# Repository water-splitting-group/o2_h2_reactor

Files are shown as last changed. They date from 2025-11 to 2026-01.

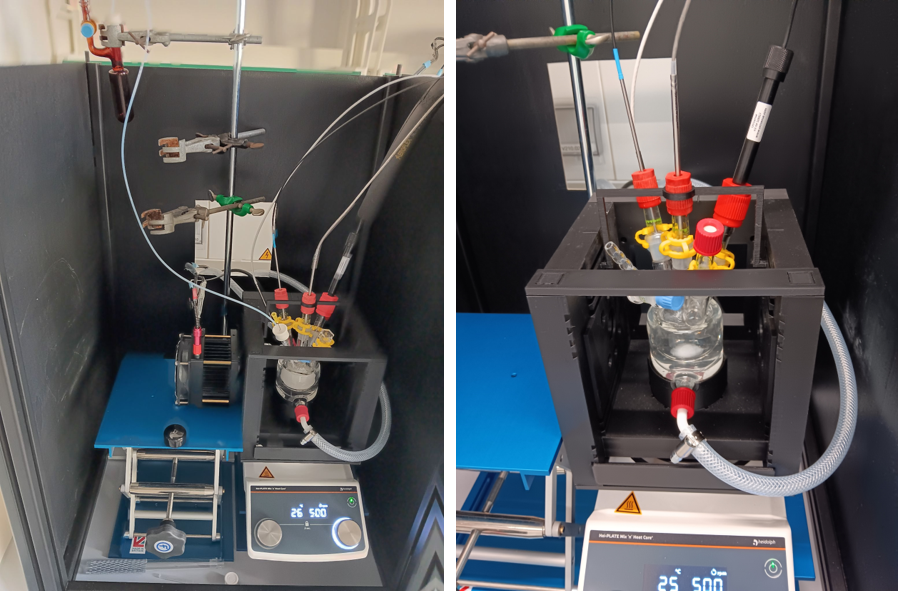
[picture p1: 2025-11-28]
figures/irrad_setup_chamber.png

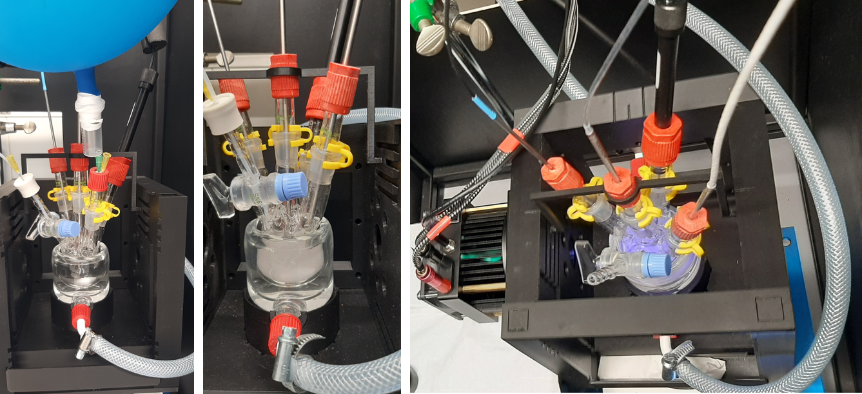
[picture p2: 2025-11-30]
figures/test_main_steps.png

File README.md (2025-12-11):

# Overview

This repository contains original data and analysis code for "Simultaneous in situ oxygen and hydrogen detection during photocatalytic water splitting".

`documents` contains manuscript and supporting information.

`experimental_data` contains experimental data, both from photocatalytic experiments, and photocatalyst characterization.

`figures` contains figures that appear in  manuscript and supporting information.

`irradiation_setup` contains files and instructions to build the setup provided in the manuscript.

`labjournal_entries` contains electronic labjournal entries of all relevant photocatalytic and synthetic experiments, general protocols (including calibration procedures, standard procedures for in situ measurements etc.), design and 3D printing of the setup compartments, as well as the devices entries in the form of .pdf files.

Subdirectories contain separate README.md files which detail their contents.

We actively encourage others to work on this interesting new avenue in automatization, are happy to answer questions or comments and are open to cooperations in this field.

# License

Copyright (c) Nadzeya Brezhneva, Alexander Eith, Ebrahim Abedini, Jacob Schneidewind

All software is licensed under a MIT license (see `LICENSE` file).

Shield: [][cc-by]

All other files and their contents are licensed under a
[Creative Commons Attribution 4.0 International License][cc-by]. (see `LICENSE-CC-BY`)

[][cc-by]

[cc-by]: http://creativecommons.org/licenses/by/4.0/
[cc-by-image]: https://i.creativecommons.org/l/by/4.0/88x31.png
[cc-by-shield]: https://img.shields.io/badge/License-CC%20BY%204.0-lightgrey.svg

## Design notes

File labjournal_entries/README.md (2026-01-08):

# General

This directory contains labjournal entries.

`equipment` contains labjournal entries of the used devices 

`general_protocols` contains labjournal entries of the used general protocols 

`irradiation_experiments` contains labjournal entries for all photocatalytic tests

`irradiation setup` contains labjournal entries for construction of irradiation chambers, 4-neck photoreactor

`synthesis_experiments` contains labjournal entries for photocatalyst preparation

`calibration_experiments` contains labjournal entries for calibration of Unisense and Pyroscience sensors

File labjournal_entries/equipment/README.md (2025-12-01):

# General

This directory contains labjournal entries of the used devices.

`3d_printer` contains info about model of the used 3D printer,

`18a_power_source` contains info about power supply,

`365_uhp_led` contains info about 365 nm LED,

`firesting_o2_meter` contains info about oxygen meter,

`h2_sensor` contains info about sensor used for hydrogen measurements in gas and liquid phase,

`irradiation_chamber` contains info about advanced irradiation chamber where irraiation was performed,

`irradiation_setup` contains info about irradiation setup where irradiation and measurements were performed,

`o2_h2_reactor` contains info about 4-neck photoreactor for O2 and H2 simultaneous measurements,

`power_meter` contains info about power meter and thermopile sensor used for adjusting LED power before photocatalytic tests,

`robust_probe_o2` contains info about sensor used for oxygen measurements in gas and liquid phase,

`unisense_h2_meter`contains info about amplifier for H2 sensor,

`vortexer` contains info about vortex mixer used for photocatalyst suspension preparation

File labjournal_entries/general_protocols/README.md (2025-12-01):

# General

This directory contains labjournal entries of the general procedures used in work.

`firesting_software` contains info about procedure for in situ O2 measurements using Pyroscience Workbench software,

`gas_phase_h2_calib` contains info about procedure of H2 sensor calibration in gas phase,

`hydrogen` contains info about the procedure of getting and transfer of H2 gas using balloon,

`in-situ_h2_o2_measurement` contains info about main steps for simultaneous in situ O2 and H2 measurements in photocatalytic tests,

`liquid_phase_h2_calib` contains info about procedure of H2 sensor calibration in liquid phase,

`power_determination` contains info about determination of the required analogue setting of power source for desired power output,

`settings_3d_printer` contains overview of standard settings for 3D printer,

`use_3d_printer` contains the procedure of 3D printing of the desired model

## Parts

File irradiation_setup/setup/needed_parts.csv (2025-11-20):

part | amount needed
aluminium profiles (nut 8, type I, black) 40x40x400 mm | 2
aluminium profiles (nut 8, type I, black) 40x40x420 mm | 2
aluminium profiles (nut 8, type I, black) 40x40x700 mm | 4
wood plate 675x443x6 mm | 2
wood plate 675x493x6 mm | 1
wood plate 675x493x6 mm, with cutout 220 mm above bottom edge 150x150 mm | 1
wood plate 550x500x6 mm | 1
lab jack | 2
laboratory stand | 1

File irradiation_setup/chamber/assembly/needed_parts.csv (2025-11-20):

part | amount needed
back_wall_v1-0 | 1
side_walls_v1-0 | 1
bottom_wall_v1-0 | 1
aperture_double_walled_beaker_v1-0 | 1
aperture_dummy_v1-0 | 1
aperture_led_v1-0 | 1
holder_o2_h2_reactor_v1-0 | 1
stabilizer_v1-0 | 2
3mm nuts DIN439 | 8
M3x25 screws DIN912 | 8
double_walled_beaker | 1
power strips | 2
LCS-0365-76-22 super high power LED from Mightex | 1
BLS-18000-1 power supply from Mightex | 1
water tubing | approx. 2 meters
LOOP Thermoelectric thermostat L100 thermostat from Lauda | 1
tubing connectors | 4

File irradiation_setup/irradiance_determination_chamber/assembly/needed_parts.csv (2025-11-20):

part | amount needed
back_wall_v1-1 | 1
side_walls_v1-0 | 1
bottom_wall_v1-0 | 1
front_wall_v1-0 | 1
lid_v1-0 | 1
aperture_dummy_v1-0 | 1
aperture_led_v1-0 | 1
aperture_power_sensor_v1-0 | 1
holder_power_sensor_v1-0 | 1
3mm nuts DIN439 | 8
M3x25 screws DIN912 | 8
LCS-0365-76-22 super high power LED from Mightex | 1
BLS-18000-1 power supply from Mightex | 1
843-R-USB power meter from Newport | 1
919P-020-12 power sensor from Newport | 1

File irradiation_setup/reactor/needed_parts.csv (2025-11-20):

part | amount needed
reactor | 1
transition piece NS14 to GL14 | 4
transition piece NS14 to GL18 | 1

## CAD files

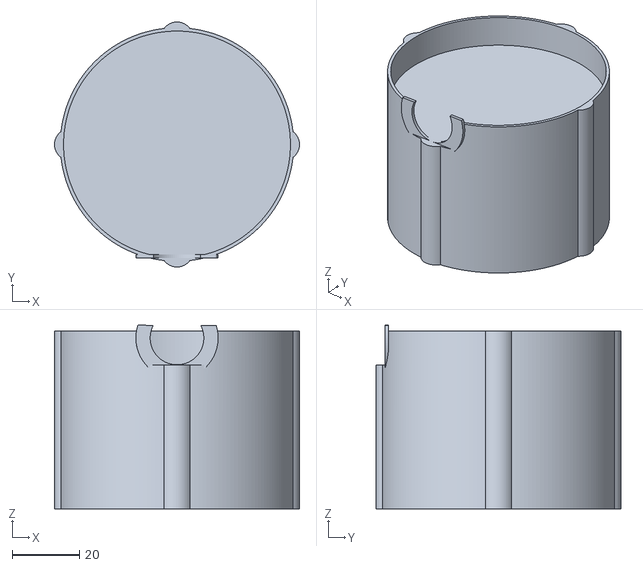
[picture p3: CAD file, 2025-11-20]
irradiation_setup/chamber/apertures/aperture_double_walled_beaker_v1-0.stl
73.0 x 73.0 x 54.7

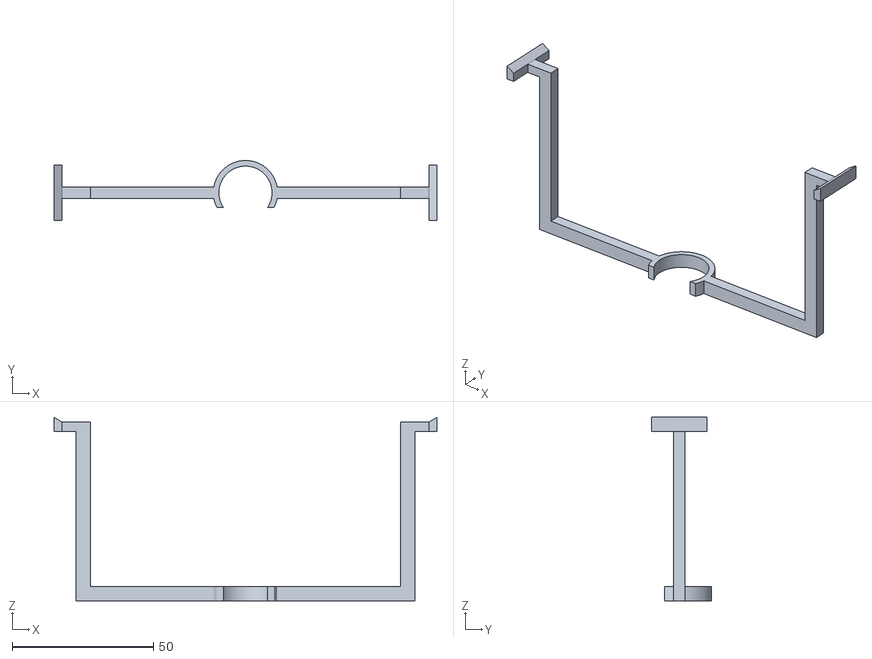
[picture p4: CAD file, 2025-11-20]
irradiation_setup/chamber/holder/holder_o2_h2_reactor_v0-3.stl
135.6 x 21.2 x 65.0

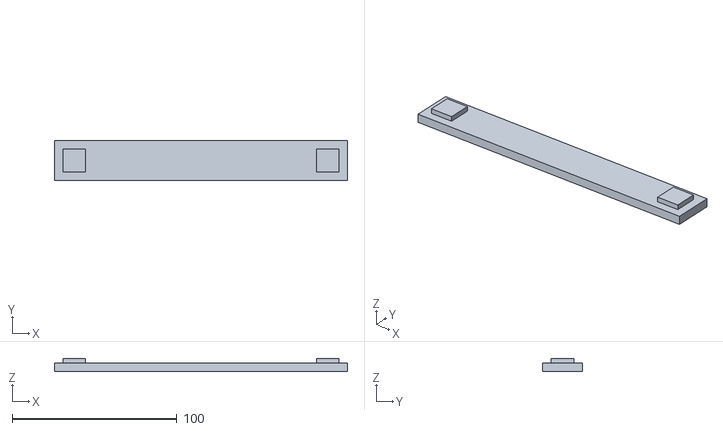
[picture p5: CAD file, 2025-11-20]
irradiation_setup/chamber/other/stabilizer_v1-0.stl
178.0 x 24.0 x 7.85

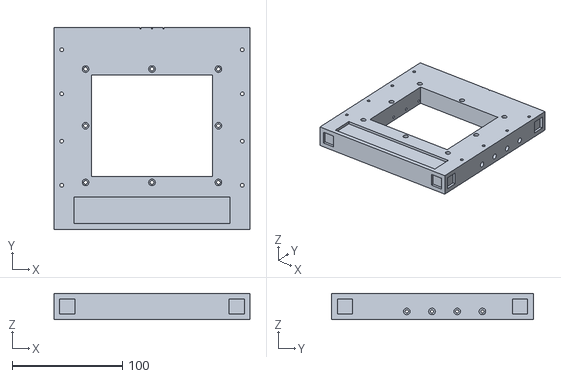
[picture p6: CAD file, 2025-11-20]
irradiation_setup/chamber/walls/back_wall_v1-0.stl
178.0 x 183.0 x 24.0

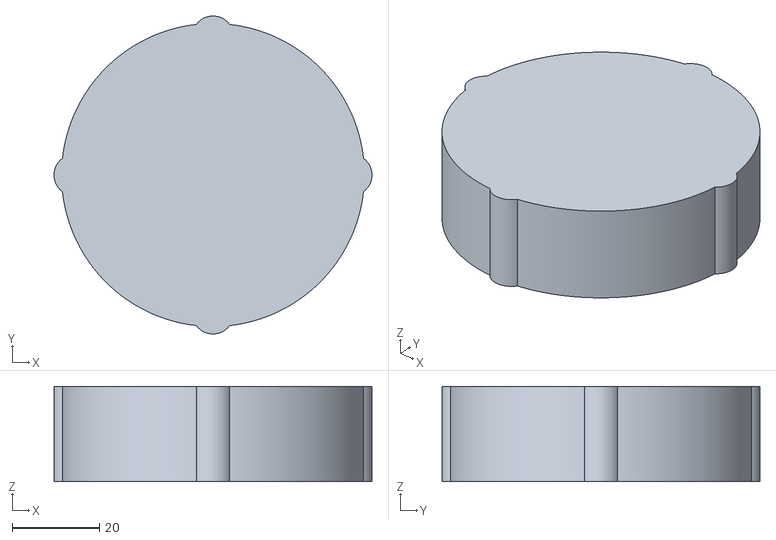
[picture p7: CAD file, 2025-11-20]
irradiation_setup/irradiance_determination_chamber/apertures/aperture_dummy_v1-0.stl
73.0 x 73.0 x 21.9

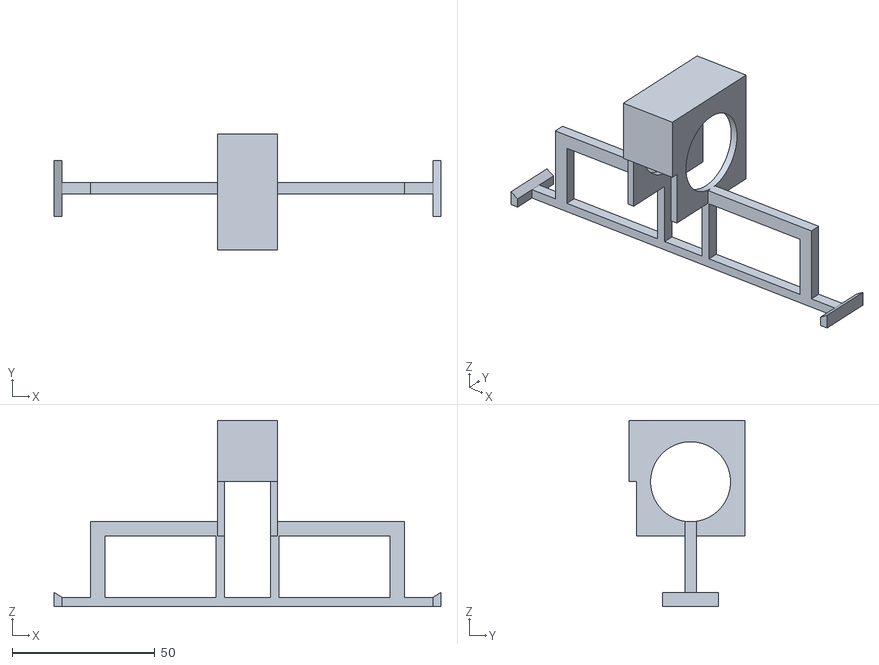
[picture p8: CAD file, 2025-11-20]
irradiation_setup/irradiance_determination_chamber/holder/holder_power_sensor_v1-0.stl
135.6 x 40.5 x 65.2

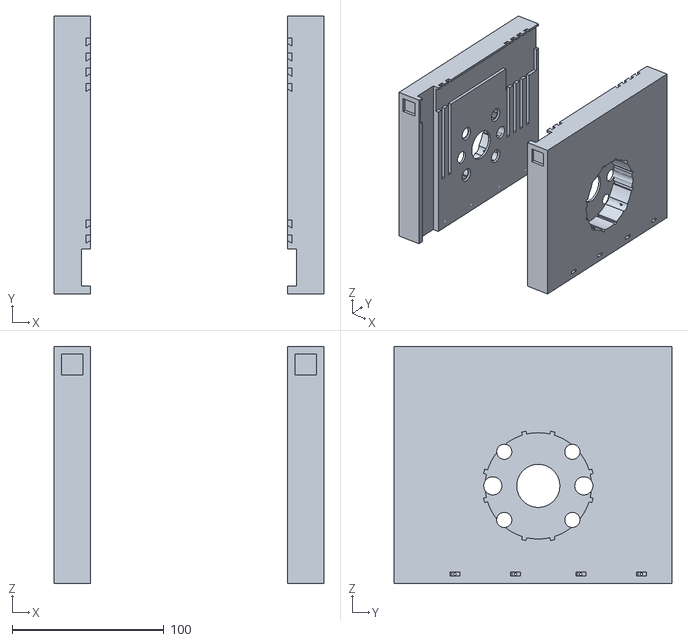
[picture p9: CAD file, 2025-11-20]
irradiation_setup/irradiance_determination_chamber/walls/side_walls_v1-0.stl
178.0 x 183.0 x 156.5

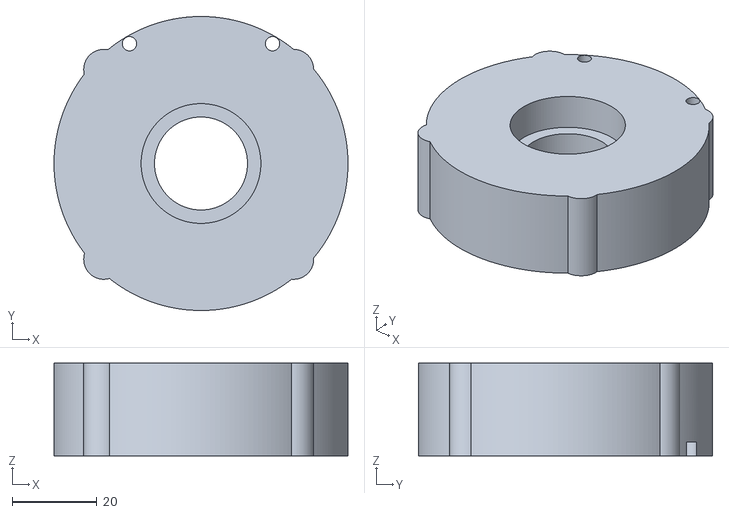
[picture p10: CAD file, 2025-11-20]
irradiation_setup/irradiance_determination_chamber/apertures/aperture_led_v1-0.stl
69.5 x 69.5 x 21.9

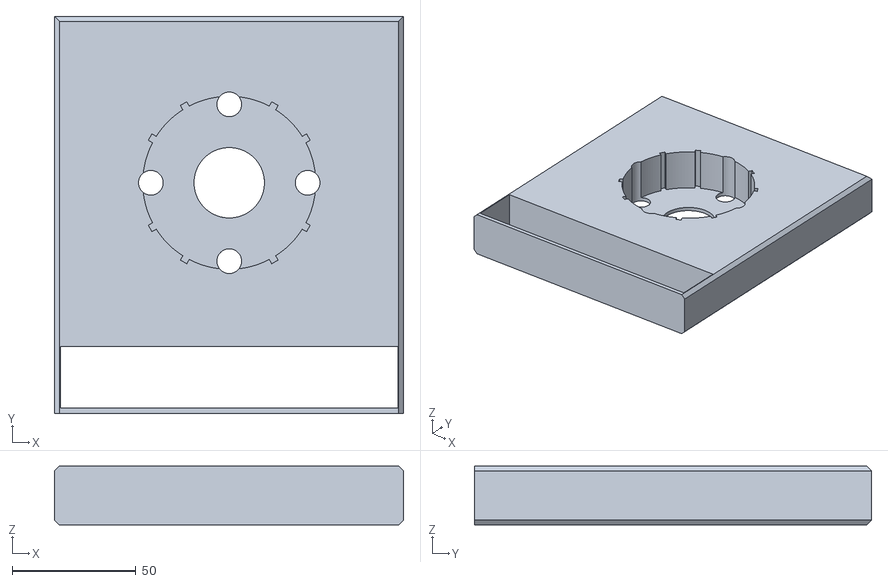
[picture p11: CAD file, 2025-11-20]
irradiation_setup/irradiance_determination_chamber/walls/bottom_wall_v1-0.stl
141.3 x 160.8 x 23.9

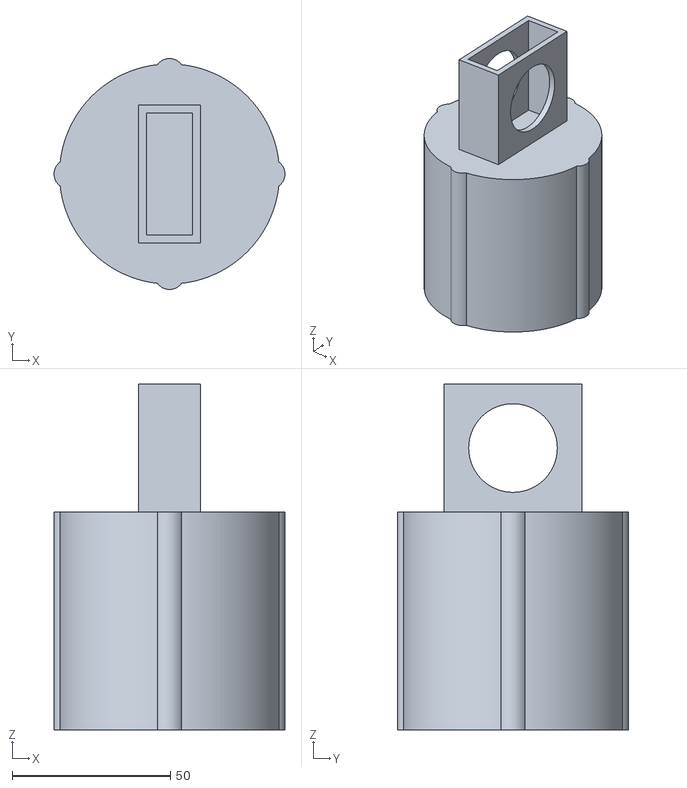
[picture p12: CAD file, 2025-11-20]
irradiation_setup/irradiance_determination_chamber/apertures/aperture_power_sensor_v1-1.stl
73.0 x 73.0 x 109.4

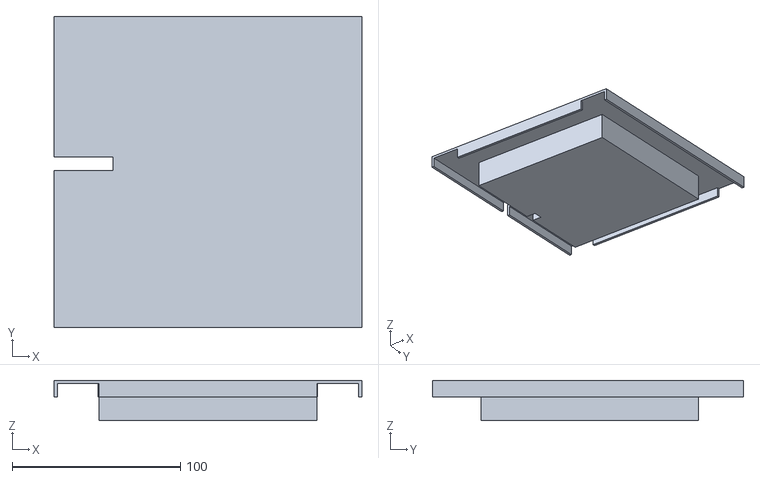
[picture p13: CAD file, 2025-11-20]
irradiation_setup/irradiance_determination_chamber/walls/lid_v1-0.stl
182.9 x 184.9 x 24.0

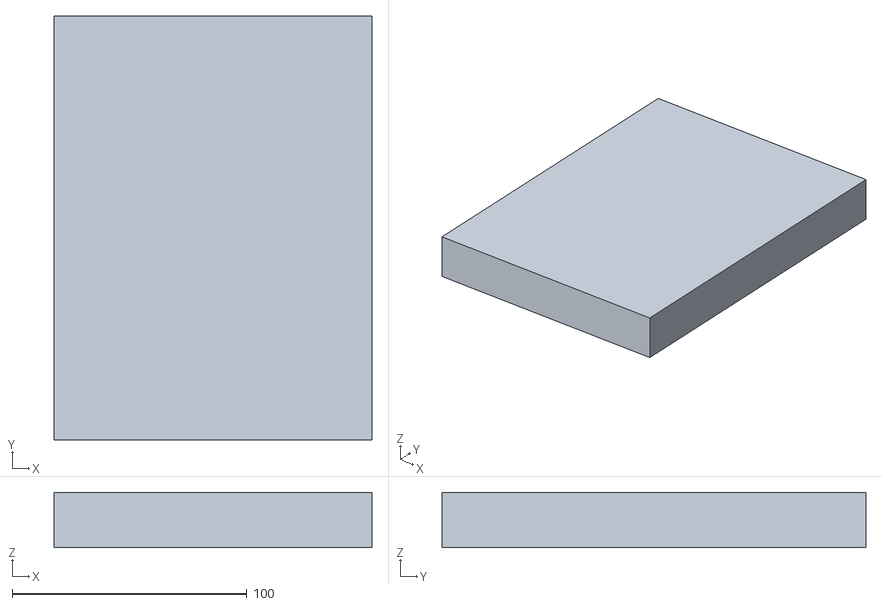
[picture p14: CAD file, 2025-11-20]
irradiation_setup/irradiance_determination_chamber/walls/front_wall_v1-0.stl
135.5 x 180.5 x 23.5

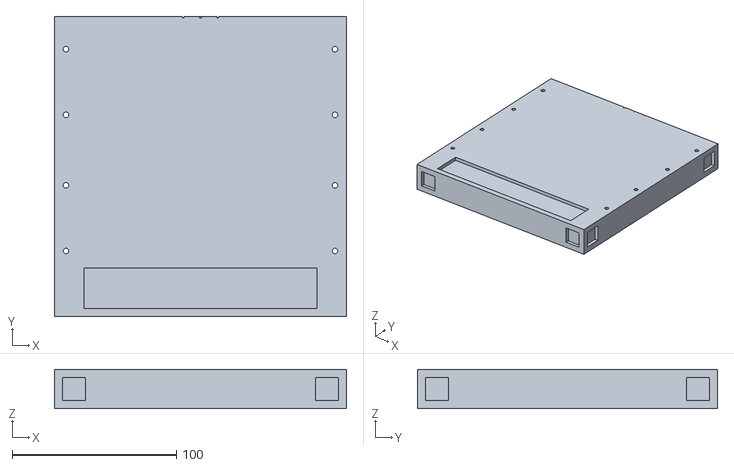
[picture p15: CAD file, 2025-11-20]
irradiation_setup/irradiance_determination_chamber/walls/back_wall_v1-1.stl
178.0 x 183.0 x 24.0

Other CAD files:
irradiation_setup/chamber/apertures/aperture_double_walled_beaker_v1-0.ipt
irradiation_setup/chamber/holder/holder_o2_h2_reactor_v0-3.ipt
irradiation_setup/chamber/other/stabilizer_v1-0.ipt
irradiation_setup/chamber/walls/back_wall_v1-0.ipt
irradiation_setup/irradiance_determination_chamber/apertures/aperture_dummy_v1-0.ipt
irradiation_setup/irradiance_determination_chamber/apertures/aperture_led_v1-0.ipt
irradiation_setup/irradiance_determination_chamber/apertures/aperture_power_sensor_v1-1.ipt
irradiation_setup/irradiance_determination_chamber/holder/holder_power_sensor_v1-0.ipt
irradiation_setup/irradiance_determination_chamber/walls/back_wall_v1-1.ipt
irradiation_setup/irradiance_determination_chamber/walls/bottom_wall_v1-0.ipt
irradiation_setup/irradiance_determination_chamber/walls/front_wall_v1-0.ipt
irradiation_setup/irradiance_determination_chamber/walls/lid_v1-0.ipt
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

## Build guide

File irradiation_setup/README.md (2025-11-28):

# General

This directory contains the files and instructions needed to build the irradiation setup

`chamber` contains the files and instructions needed to build the irradiaiton chamber

`irradiance_determination_chamber` contains the files and instructions to build the irradiance determination chamber

`reactor` contains the files and instructions to build the reactor

`setup` contains the instructions to build the irradiaiton setup, meaining the wooden enclousre and parts beside the chamber and reactor installed in the complete setup

`synthesis` contains the labjournal entries of the synthesis of the ligands and complexes

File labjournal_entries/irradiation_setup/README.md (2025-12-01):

# General

This directory contains labjournal protocols related to irradiation setup.

`AE-515` contains info about procedure for 3D printing of components of advanced irradiation setup,

`AE-516`contains protocol for design and printing of holder for 4-neck photoreactor (BOLA GL14 cap for PT1000 sensor),

`AE-541` contains info about design and printing of protective cover of H2 sensor,

`AE-594` contains info about design and printing of holder for power measurements

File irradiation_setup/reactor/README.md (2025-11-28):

# General

This directory contains the files and instructions needed to build the reactor

`description_reactor` is a txt file detailing the description of the reactor

`needed_parts` is a list of the needed parts to build the reactor, without sensors

`sketch_reactor` is a photo of the reactor with measurments written next to it

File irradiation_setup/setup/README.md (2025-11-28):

# General

This directory contains the files and instructions needed to build the reactor

`assembly` is a txt file detailing the assembly of the setup without the chamber and reactor

`needed_parts` is a list of the needed parts to build the setup without the chamber and reactor

`pciture_setup` is a photo of the fully equipped setup

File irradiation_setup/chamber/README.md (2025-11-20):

# General

This directory contains the files and instructions needed to build the irradiation chamber

`aperture` contains the CAD and STL files for the needed apertures

`assambly` contains the instructions to build the chamber and a list of all needed parts

`holder` contains the CAD and STL files for the needed holder

`other` contains the CAD and STL files for the needed other 3D printed parts, as well as a ocitrue and description of the double walled beaker

`walls` contains the CAD and STL files for the needed walls

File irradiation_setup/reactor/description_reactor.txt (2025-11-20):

outer Diameter of Bottom part is 40 mm
height till start of necks approx. 40 mm
necks are arranged in cross-shape
1 neck has NS14.5 Valve with 4 mm bore
neck opposite to that has NS14 outer Joint and maximal height below 50 mm
other 3 necks have NS14 outer Joint with total height of approx. 60 mm

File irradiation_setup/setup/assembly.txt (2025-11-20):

1. connect aluminium profiles to each other to build the frame
2. slide in side walls and back wall
3. add 2 lab jacks and a laboratory stand
4. add stirring plate ontop of 1 lab jack

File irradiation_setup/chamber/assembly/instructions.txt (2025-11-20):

1. print all needed parts and remove the support
2. add 3mm nuts in the holes in the side walls (see figure 1). Make sure that the nuts are as far down as possible
3. add M3x25 screws in the side walls (see figure 2)
4. screw the side walls to the back wall
5. add stabilizors on the Bottom of the side wall and the back wall (see figure 3)
6. slide in bottom wall (see figure 4)
7. add aperture for double walled beaker in to hole in the Bottom wall (see figure 5)
8. add apertures for LED and dummy aperture to holes the side walls
9. move the chamber into a Irradiation setup
10. add double walled beaker into aperture for double walled beaker and secure it with power strips to the aperture
11. add tubing to the double walled beaker, connect it to the Thermostat and fill it with coolant
12. slide in LED into aperture for LED
13. connect the LED to the power supply

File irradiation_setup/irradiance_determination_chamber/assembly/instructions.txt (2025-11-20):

1. print all needed parts and remove the support
2. add 3mm nuts in the holes in the side walls (see figure 1). Make sure that the nuts are as far down as possible
3. add M3x25 screws in the side walls, analog to the Irradiation chamber
4. screw the side walls to the back wall (see figure 2)
5. slide in bottom wall (see figure 3)
6. add aperture or holder for power sensor (see figure 4)
7. add front wall (see figure 5)
8. add apertures for LED and dummy aperture to holes the side walls
9. add power sensor to holder or aperture for power sensor
10. add lid (see figure 6, power sensor not installed in Picture)
11. connect power sensor to power meter
12. slide in LED into aperture for LED
13. connect the LED to the power supply

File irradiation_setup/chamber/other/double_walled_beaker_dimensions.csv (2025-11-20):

measurement | value | unit
height_outer_beaker | 55-60 | mm
height_inner_beaker | 50 | mm
diameter_outer_beaker | 60-65 | mm
diameter_inner_beaker | 45 | mm
thickness_wall | 1-2 | mm
position_GL14_inlet_from_bottom | 5 | mm
position_GL14_outlet_from_top | 5 | mm

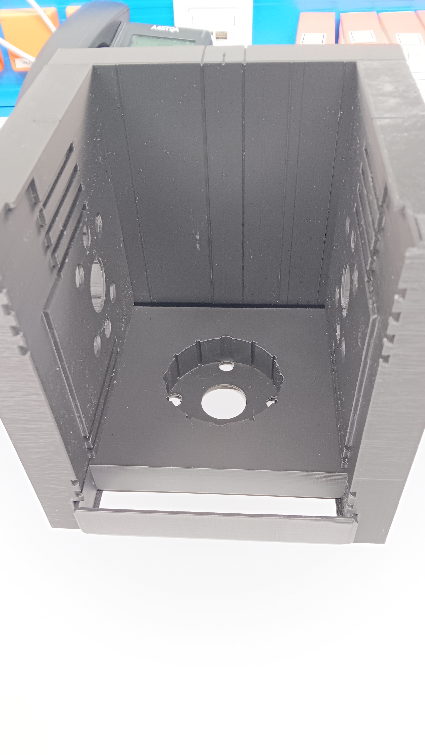
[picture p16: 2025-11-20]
irradiation_setup/irradiance_determination_chamber/assembly/figure_3.jpg

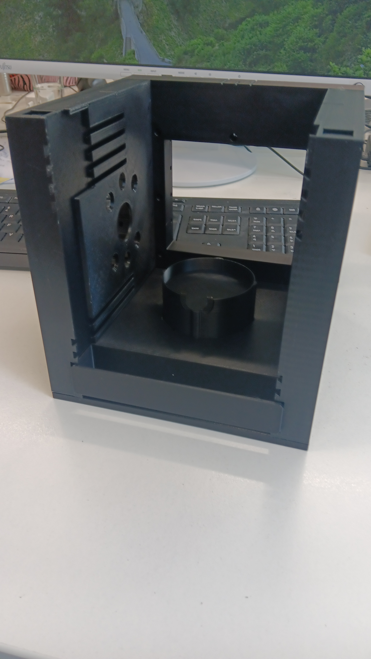
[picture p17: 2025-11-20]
irradiation_setup/chamber/assembly/figure_5.jpg

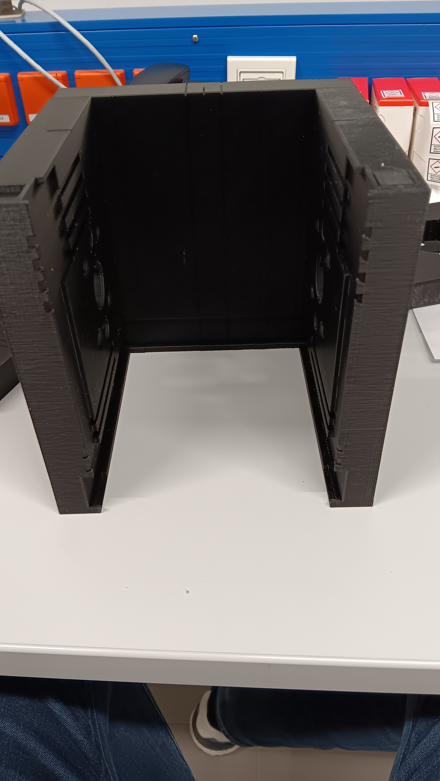
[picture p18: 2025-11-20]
irradiation_setup/irradiance_determination_chamber/assembly/figure_2.jpg

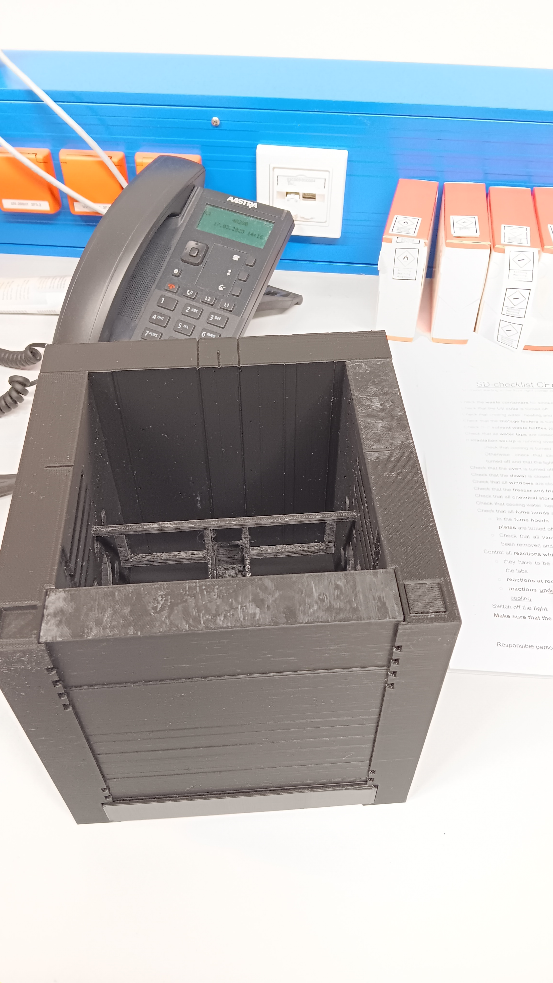
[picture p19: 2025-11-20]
irradiation_setup/irradiance_determination_chamber/assembly/figure_5.jpg

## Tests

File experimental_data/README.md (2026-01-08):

Contains experimental data from photocatalytic tests and photocatalyst characterization.

`calibration_data`contains original and processed data from calibration of oxygen and hydrogen sensors.

`characterization_data`contains original and processed data from SEM, XRD and BET analyses.

`irradiation_data`contains original data from simultaneous H2 and O2 measurements, containing raw data for each O2 measurement and each H2 measurement per photocatalytic test with summary in Excel file.

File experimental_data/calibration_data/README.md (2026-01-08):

Contains experimental data from calibration of oxygen and hydrogen sensor.

`GC_Unisense`contains original and processed data from gas phase H2 measurements with gas chromatography and Unisense sensor.

`H2_gas_phase`contains original and processed data from calibration of Unisense sensor in gas phase.

`H2_liquid_phase`contains original and processed data from calibration of Unisense sensor in liquid phase.

`O2_calibration`contains original data from calibration of Pyroscience sensor.

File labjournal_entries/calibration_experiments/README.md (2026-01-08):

Contains protocols related to the calibration of Unisense H2 sensor and Pyroscience O2 sensor in gas and liquid phase.

| Type of calibration  | Experiment names |
| ----------- | ---------------- |
| Unisense sensor (gas phase) | AE-530 |
| Unisense sensor (gas phase, comparison with GC)  | NB-AE-222 |
| Unisense sensor (liquid phase) | AE-533 |
| Pyroscience sensor (gas phase)  | NB-280 |
| Pyroscience sensor (liquid phase)  | NB-234 |

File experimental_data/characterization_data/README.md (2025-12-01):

Contains data from photocatalyst characterization.

`SEM`contains original scanning electron microscope images (different magnifications) of the photocatalyst in the form of .tiff files and figure in the form of .png file.

`XRD`contains original data from X-ray diffraction analysis of the photocatalyst and diffractogram of the sample in the form of .png file.

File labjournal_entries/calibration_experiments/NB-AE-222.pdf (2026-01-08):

PDF generated with elabftw, (https://www.elabftw.net) a free and open source lab notebook File generated on 08-01-2026 at 09:39

## NB-AE-222: Gas phase H2 measurements with Unisense H2 sensor, GC calibration

Date: 2025-05-16
Tags: | Test | AE | Calibration | Future | NB | GC
H2 | Gas chromatography | Unisense | H2
Sensor | In situ
Category: SrTiO3
Status: Done
Created by: Nadzeya Brezhneva

### Literature/reference experiments

Literature | /
Reproduction | /

Similar
experiments

SrTiO3 - AE-483: Testing of in-situ electrochemical hydrogen sensor and test H2 evolution reaction with RhCrO:Al:SrTiO3 (https://elab.water-splitting.org/experiments.php?mode=view&id=2087)
SrTiO3 - AE-484: Testing of in-situ electrochemical hydrogen sensor and test H2 evolution reaction with RhCrO:Al:SrTiO3 (https://elab.water-splitting.org/experiments.php?mode=view&id=2107)
SrTiO3 - NB-AE-215 / AE-485: Gas phase H2 measurements with H2 sensor, SrTiO3:Al loaded with RhxCryO3 (NB-162-4) suspension (1 mg/ml), 365 nm UHP LED, check with GC measurements (https://elab.water-splitting.org/experiments.php?mode=view&id=2119)

### Reagents

Name | CAS Number / Experiment Number | Inventory number | Amount [mmol] | Equivalents | Masstheo [mg] | Massexp [mg] | Molar mass [g/mol] | Density (g/ml) | Volume [ml] | pressure [bar]
milli-Q H2O | / | / | / | / | / | / | / | / | ca. 5 (for H2 saturated atmosphere in the RBF) | /
Hydrogen | 1333-74-0 (https://commonchemistry.cas.org/detail?ref=1333-74-0) | / | / | / | / | / | / | / | 1 ballon (approx. 2 L) | approx. 1

### Procedure/observations

Date | Time | Step | Observations | Pictures
21.05.2025 | ca. 10:10 | The Device was connected to the computer and the device was conected to the sensor and the PT100.The experiment was started on the device - the PreAmp was set at 1pA=1mV and the polarisation was 100 mV | / | /
| ca. 10:25 | The logging was started (sample interval for pre-measurements was set 10 s). | NB-AE-222-Logger1 | /
| 10:25 | Attempt to connect PT 100 sensor. | Problems with recognizing PT 100, by now no use of the sensor. | /
| ca. 10:30 | A 10 mL RBF flask was filled with Milli-q water (approx. 5 mL) (flask 1) | / | 20250521_104013-RBF-with-H2O.jpg
| ca. 10:45-50 | Filling the balloon with H2 gas in E005 lab according to the protocol Protocol - Getting hydrogen from hydrogen bottle in CEEC II E014 (https://elab.water-splitting.org/database.php?mode=view&id=223) | / | /
| ca.10:50 | Start purging flask 1 with H2 from the balloon (two cannulas in the septum) according to the protocol Protocol - Gas phase calibration of H2 UniAmp sensor. (https://elab.water-splitting.org/database.php?mode=view&id=225) | / | 20250521_105118-H2-purging-with-balloon.jpg
| ca. 11:05 | Important note: removing the second needle to from the balloon. reduce too fast release of H2 | / | /
| 11:10-12:40 | Continuous recording during pre-measurements were continued. | / | Unisense-pre-measurements-Screenshot-2025-05-21-160016.png

12:40 | PT 100 sensor was connected. | Now everything went well, the sensor is recognized. | /
12:46 | The logging was stopped | / | /
ca. 12:50 | The H2 sensor was placed on a Gl14/NS14 5 mL Schlenk flask (flask 2) equipped with a PTFE stirring bar insisde ( Prep work - AE-482: Volume determination of GL14/NS14 5 mL Schlnek flask) (https://elab.water-splitting.org/experiments.php?mode=view&id=2077) using a 2.0 mm BOLA fitting | / | 20250521_130448-GL14-NS14-flask-setup.jpg 20250521_130207-with-H2-sensor.jpg
13:02 | Start stirring (400 rpm), LAUDA on (25 °C), PT 100 sensor was placed inside the water bath.
13:06 | A new logging was started. | NB-AE-222-Logger2 | /
13:12 | The first calibration point was taken at 0 ppm H2 | Calibration --> Offset --> Set value close to 0 (in current experiment -4 mV). | Unisense-calibration-Screenshot-2025-05-21-160445.png
| Calculations of the amount of saturated H2 gas that is needed to be injected into a GL14/NS14 flask Vtotal (GL14/NS14) = 11.66 mL according to Prep work - AE-482: Volume determination of GL14/NS14 5 mL Schlnek flask (https://elab.water-splitting.org/experiments.php?mode=view&id=2077) 0.05 % (Vtotal) = 0.0058 mL = 5.8 µL (6 µL) 0.3 % (Vtotal) = 0.0348 mL = 34.8 µL (35 µL) 1% (Vtotal) = 0.116 mL = 116 µL
13:25 | 6 uL of H2 saturated gas was taken from the head space of flask 1 using 100 µL Pressure lok syringe and injected into flask 2 (via septum on the NS14 neck). | / | /
13:25-27 | Waiting for ca. 1-2 min for stabilizing the signal, afterwards adding point to the calibration curve (corresponded to the signal 2.8 mV).
13:29 | Taking 100 uL of the sample from the head space of GL14/NS14 flask (preliminary flushing it with the gas phase from the head space) and kept in Pressure lok syringe for further investigations with GC. | NB-AE-222-gas 0.05 %theor H2 | Unisense-signal-vs-time-Screenshot-2025-05-21-155932.png
13:30-35 | The sample was transferred to GC lab (314) in TO Building.
ca. 13:50 | GC measurements of the sample NB-AE-222-gas 0.05 %theor H2 with Equipment - GC chromatograph Schimadzu Nexis GC-2030, Peneva`s Lab 304, Physical Chemistry building (https://elab.water-splitting.org/database.php?mode=view&id=125) in accordance with the protocol Protocol -Hydrogen Measurement Using GC. (https://elab.water-splitting.org/database.php?mode=view&id=126) | Change of septum in the GC --> delay in start of the measurements in ca. 15 min | /
14:07 | For 0.3 vol.% H2 in total volume, 29 uL H2 saturated gas was taken from the head space of flask 1 using Pressure lok syringe and injected into flask 2 (via septum on the NS14 neck). | Since the signal after first injection of H2 sat gas was stable, it was necessary to inject just 29 uL (35 uL-6 uL) instead of the required 35 uL | /
| Important note: adjust the parameters in H2 table each time before injecting the sample (check current values of temperatute 24.5°C and pressure 991 mbar). The input of the value in ppm will give the result in Pa at the bottom of the panel. | Screenshot-2025-05-27-184655-Unisense calculator.png | /
14:08 | Waiting for 1 min for stabilizing signal, addition of the third point to the calibration curve. | / | /
ca. 14:10 | Taking 100 uL of the sample from the head space of GL14/NS14 flask (preliminary flushing it with the gas phase from the head space) and kept in Pressure lok syringe for further investigations with GC. | NB-AE-222-gas 0.3 %theor H2 | Unisense-signal-vs-time-Screenshot-2025-05-21-155932.png
ca. 14:10-15 | The sample was transferred to GC lab (314) in TO Building. | / | /
ca. 14:20 | GC measurements of the sample NB-AE-222-gas 0.3 %theor H2 with Equipment - GC chromatograph Schimadzu Nexis GC-2030, Peneva`s Lab 304, Physical Chemistry building (https://elab.water-splitting.org/database.php?mode=view&id=125) in accordance with the protocol Protocol -Hydrogen Measurement Using GC. (https://elab.water-splitting.org/database.php?mode=view&id=126) | / | /
ca. 14:30 | For 1 vol.% H2 in total volume, 82 uL H2 saturated gas was taken from the head space of flask 1 using Pressure lok syringe and injected into flask 2 (via septum on the NS14 neck). | Since the signal after the second injection of H2 sat gas was stable, it was necessary to inject just 82 uL (117 uL-35 uL) instead of the required 117 uL | /
ca. 14:32 | Waiting for ca. 1-2 min for stabilizing signal, addition of the fourth point to the calibration curve. | / | /

| ca. 14:35 | Taking 100 uL of the sample from the head space of GL14/NS14 flask (preliminary flushing it with the gas phase from the head space) and kept in Pressure lok syringe for further investigations with GC. | NB-AE-222-gas 1 %theor H2 | Unisense-signal-vs-time-Screenshot-2025-05-21-155932.png
| ca. 14:40 | The sample was transferred to GC lab (314) in TO Building. | / | /
| ca. 14:50 | GC measurements of the sample NB-AE-222-gas 1 %theor H2 with Equipment - GC chromatograph Schimadzu Nexis GC-2030, Peneva`s Lab 304, Physical Chemistry building (https://elab.water-splitting.org/database.php?mode=view&id=125) in accordance with the protocol Protocol -Hydrogen Measurement Using GC. (https://elab.water-splitting.org/database.php?mode=view&id=126) | / | /
| ca. 15:20 | The calibration was applied | / | /
| 15:22 | The logging was stopped and subsequently the experiment was stopped | /
| ca. 15:40 | Deassembling the setup. | / | /
22.05.2025 | ca. 15:40 | GC calibration using 25 uL, 50 uL, 75 uL, 100 uL H2 with 1 % All-in-gas reference gas mixture (1 vol.%) and Pressure lok syringe using Equipment - GC chromatograph Schimadzu Nexis GC-2030, Peneva`s Lab 304, Physical Chemistry building (https://elab.water-splitting.org/database.php?mode=view&id=125) in accordance with the protocol Protocol -Hydrogen Measurement Using GC. (https://elab.water-splitting.org/database.php?mode=view&id=126) | / | /

### Analysis

Date | Time | Sample name | Analysis method

Analytical

device | Solvent | Raw Data | Processed Data | Comparative
Data | Interpretation
21.05.2025 | 10:25-12:46 | NB-AE-222-Logger1 | electrochemical H2 detection

Equipment -
H2 UniAmp
Sensor (https://elab.water-splitting.org/database.php?mode=view&id=222)

/

NB-222-1.ulog (http://elab.water-splitting.org/app/controllers/app/download.php?name=NB-222-1.ulog&storage=1)
NB-AE-222-log1-pre-measurements.xlsx (http://elab.water-splitting.org/app/controllers/app/download.php?name=NB-AE-222-log1-pre-measurements.xlsx&storage=1) Calibration-data-for-pre-measurements.csv (http://elab.water-splitting.org/app/controllers/app/download.php?name=Calibration-data-for-pre-measurements.csv&storage=1) Comments-pre-measurements.csv (http://elab.water-splitting.org/app/controllers/app/download.php?name=Comments-pre-measurements.csv&storage=1) Data-1-H2-UniAmp-503157-pre-measurements.csv (http://elab.water-splitting.org/app/controllers/app/download.php?name=Data-1-H2-UniAmp-503157-pre-measurements.csv&storage=1) Devices-pre-measurements.csv (http://elab.water-splitting.org/app/controllers/app/download.php?name=Devices-pre-measurements.csv&storage=1) Miscellaneous-pre-measurements.csv (http://elab.water-splitting.org/app/controllers/app/download.php?name=Miscellaneous-pre-measurements.csv&storage=1)

Unisense-pre-measurements-Screenshot-2025-05-21-160016.png /

Pre-measurements are done, the signal is stable during measurements.

13:06-15:35 | NB-AE-222-Logger2 | electrochemical H2 detection

Equipment -
H2 UniAmp
Sensor (https://elab.water-splitting.org/database.php?mode=view&id=222)

/

NB-222-1.ulog (http://elab.water-splitting.org/app/controllers/app/download.php?name=NB-222-1.ulog&storage=1)
NB-AE-222-log2-calibration.xlsx (http://elab.water-splitting.org/app/controllers/app/download.php?name=NB-AE-222-log2-calibration.xlsx&storage=1) Calibration-data-for-calibration.csv (http://elab.water-splitting.org/app/controllers/app/download.php?name=Calibration-data-for-calibration.csv&storage=1) Comments-for-calibration.csv (http://elab.water-splitting.org/app/controllers/app/download.php?name=Comments-for-calibration.csv&storage=1) Data-1-H2-UniAmp-503157-for-calibration.csv (http://elab.water-splitting.org/app/controllers/app/download.php?name=Data-1-H2-UniAmp-503157-for-calibration.csv&storage=1) Devices-for-calibration.csv (http://elab.water-splitting.org/app/controllers/app/download.php?name=Devices-for-calibration.csv&storage=1) Miscellaneous-for-calibration.csv (http://elab.water-splitting.org/app/controllers/app/download.php?name=Miscellaneous-for-calibration.csv&storage=1)

Unisense-calibration-Screenshot-2025-05-21-160445.png Unisense-signal-vs-time-Screenshot-2025-05-21-155932.png Unisense-calculations.xlsx (http://elab.water-splitting.org/app/controllers/app/download.php?name=Unisense-calculations.xlsx&storage=1)

/

Signal vs. time
Step-by-step increase in
signal value after gradual injection of H2-containing mixture.
4-point calibration
R

2
= 1, intercept = -1.031,
slope = 0.078.

After processing Unisense
data:
theor 0.05 vol.% ---> 0.0517 vol.%
theor 0.3 vol.% ---> 0.3001 vol.%
theor 1 vol.% ---> 1.0004
vol.%
13:29 | NB-AE-222-gas 0.05 % theor H2 | GC | Equipment -GC chromatograph Schimadzu Nexis GC-2030, Peneva`s Lab 304, Physical Chemistry building (https://elab.water-splitting.org/database.php?mode=view&id=125) | / | Calibration-Unisense.gcb (http://elab.water-splitting.org/app/controllers/app/download.php?name=Calibration-Unisense.gcb&storage=1) Blank1.gcd (http://elab.water-splitting.org/app/controllers/app/download.php?name=Blank1.gcd&storage=1) theor-0.05-vol.gcd (http://elab.water-splitting.org/app/controllers/app/download.php?name=theor-0.05-vol.gcd&storage=1) theor-0.05-vol-H2-GC.txt (http://elab.water-splitting.org/app/controllers/app/download.php?name=theor-0.05-vol-H2-GC.txt&storage=1) | theor-0.05-vol.-H2.PNG | / | Rough estimation by LabSolution software (conc vol.%) 0.239, much higher than expected
14:10 | NB-AE-222-gas 0.3 % theor H2 | GC | Equipment -GC chromatograph Schimadzu Nexis GC-2030, Peneva`s Lab 304, Physical Chemistry building (https://elab.water-splitting.org/database.php?mode=view&id=125) | / | Calibration-Unisense-1.gcb (http://elab.water-splitting.org/app/controllers/app/download.php?name=Calibration-Unisense-1.gcb&storage=1) Blank1.1.gcd (http://elab.water-splitting.org/app/controllers/app/download.php?name=Blank1.1.gcd&storage=1) theor-0.3-vol.gcd (http://elab.water-splitting.org/app/controllers/app/download.php?name=theor-0.3-vol.gcd&storage=1) theor-0.3-vol-H2-GC.txt (http://elab.water-splitting.org/app/controllers/app/download.php?name=theor-0.3-vol-H2-GC.txt&storage=1) | theor-0.3-vol.-H2.PNG | / | Rough estimation by LabSolution software (conc vol.%) 0.569, higher than expected
14:35 | NB-AE-222-gas 1 % theor H2 | GC | Equipment -GC chromatograph Schimadzu Nexis GC-2030, Peneva`s Lab 304, Physical Chemistry building (https://elab.water-splitting.org/database.php?mode=view&id=125) | / | Calibration-Unisense-2.gcb (http://elab.water-splitting.org/app/controllers/app/download.php?name=Calibration-Unisense-2.gcb&storage=1) Blank1.2.gcd (http://elab.water-splitting.org/app/controllers/app/download.php?name=Blank1.2.gcd&storage=1) theor-1-vol.gcd (http://elab.water-splitting.org/app/controllers/app/download.php?name=theor-1-vol.gcd&storage=1) theor-1-vol-H2-GC.txt (http://elab.water-splitting.org/app/controllers/app/download.php?name=theor-1-vol-H2-GC.txt&storage=1) | theor-1-vol.-H2.PNG | / | Rough estimation by LabSolution software (conc vol.%) 1.122, a bit higher, but comparable with expected value
22.05.2025 | 15:40 | / | GC

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

/

NB-222-calibration.gcb (http://elab.water-splitting.org/app/controllers/app/download.php?name=NB-222-calibration.gcb&storage=1)
Blank002.gcd (http://elab.water-splitting.org/app/controllers/app/download.php?name=Blank002.gcd&storage=1)
100H2-calibration-GC.gcd (http://elab.water-splitting.org/app/controllers/app/download.php?name=100H2-calibration-GC.gcd&storage=1)
100H2-calibration-GC.txt (http://elab.water-splitting.org/app/controllers/app/download.php?name=100H2-calibration-GC.txt&storage=1)
75H2-calibration-GC.gcd (http://elab.water-splitting.org/app/controllers/app/download.php?name=75H2-calibration-GC.gcd&storage=1)
75H2-calibration-GC.txt (http://elab.water-splitting.org/app/controllers/app/download.php?name=75H2-calibration-GC.txt&storage=1)
50H2-calibration-GC.gcd (http://elab.water-splitting.org/app/controllers/app/download.php?name=50H2-calibration-GC.gcd&storage=1)
50H2-calibration-GC.txt (http://elab.water-splitting.org/app/controllers/app/download.php?name=50H2-calibration-GC.txt&storage=1)
25H2-calibration-GC.gcd (http://elab.water-splitting.org/app/controllers/app/download.php?name=25H2-calibration-GC.gcd&storage=1)
25H2-calibration-GC.txt (http://elab.water-splitting.org/app/controllers/app/download.php?name=25H2-calibration-GC.txt&storage=1)

100-H2.PNG
75-H2.PNG
50-H2.PNG
25-H2.PNG

GC_Data_Analysis_H2-1.py (http://elab.water-splitting.org/app/controllers/app/download.php?name=GC_Data_Analysis_H2-1.py&storage=1)
NB_222_Data.csv (http://elab.water-splitting.org/app/controllers/app/download.php?name=NB_222_Data.csv&storage=1)
NB_222_Data-Results.txt (http://elab.water-splitting.org/app/controllers/app/download.php?name=NB_222_Data-Results.txt&storage=1)
NB_222_Data-Analysis.tiff (http://elab.water-splitting.org/app/controllers/app/download.php?name=NB_222_Data-Analysis.tiff&storage=1)

/

After calibration and
processing data in Python: according to GC:
theor 0.05 vol.% ---> 0.252 vol.%
theor 0.3 vol.% ---> 0.588 vol.%
theor 1 vol.% ---> 1.151
vol.%

### Results

H2

test measurements with Unisense hydrogen sensor was performed. GC measurements (as well as 4-point calibration with 1 vol.% H2

gas mixture) was performed as a control.

Four points were tested - 0, 0.05 vol.%, 0.3 vol.%, 1 vol.% (theoretical values)

According to the Unisense data:

theor 0.05 vol.% ---> 0.0517 vol.%

theor 0.3 vol.% ---> 0.3001 vol.%

theor 1 vol.% ---> 1.0004 vol.%

Used as calibration data for Unisense.

Check with GC (after 4 point calibration with 1 vol.% H2

gas mixture and processing data in Python):

theor 0.05 vol.% ---> 0.252 vol.%

theor 0.3 vol.% ---> 0.588 vol.%

theor 1 vol.% ---> 1.151 vol.%

Unisense data are in a very good agreement with theoretical values, whereas GC data (especially theor 0.05 vol.% and 0.3 vol.%) are not in good agreement with Unisense and theoretical values, high error.

### Future recommendations

Old procedure | Problem | Future recommendations
/ | / | placing water into Schlenk where H2 measurement is performed.
/ | / | In future: exporting only data-1 csv file from Unisense Logger software.

### Linked experiments

Prep work - AE-477: Testing of in-situ electrochemical hydrogen sensor and test H2 evolution reaction with RhCrO:Al:SrTiO3 (https://elab.water-splitting.org/experiments.php?mode=view&id=2029)

Prep work - AE-482: Volume determination of GL14/NS14 flask (https://elab.water-splitting.org/experiments.php?mode=view&id=2077)

SrTiO3 - NB-162: Preparation of SrTiO3:Al with RhyCr2-yO3 (Osterloh route), I attempt, 1000 C 10h (https://elab.water-splitting.org/experiments.php?mode=view&id=1851)

SrTiO3 - AE-483: Testing of in-situ electrochemical hydrogen sensor and test H2 evolution reaction with RhCrO:Al:SrTiO3 (https://elab.water-splitting.org/experiments.php?mode=view&id=2087)

SrTiO3 - AE-484: Testing of in-situ electrochemical hydrogen sensor and test H2 evolution reaction with RhCrO:Al:SrTiO3 (https://elab.water-splitting.org/experiments.php?mode=view&id=2107)

SrTiO3 - NB-AE-215 / AE-485: Gas phase H2 measurements with H2 sensor, SrTiO3:Al loaded with RhxCryO3 (NB-162-4) suspension (1 mg/ml), 365 nm UHP LED, check with GC measurements (https://elab.water-splitting.org/experiments.php?mode=view&id=2119)

### Linked resources

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

Equipment - H2 UniAmp Sensor - Low range - 2.1 x 80 mm needle (https://elab.water-splitting.org/database.php?mode=view&id=222)

General Protocol - Hydrogen Measurement Using GC (AG Paneva) (https://elab.water-splitting.org/database.php?mode=view&id=126)

General Protocol - Getting hydrogen from hydrogen bottle in CEEC II E014 (https://elab.water-splitting.org/database.php?mode=view&id=223)

General Protocol - Gas phase calibration of H2 UniAmp sensor (https://elab.water-splitting.org/database.php?mode=view&id=225)

Light Source - UHP LED 365 nm-1 (https://elab.water-splitting.org/database.php?mode=view&id=46)
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

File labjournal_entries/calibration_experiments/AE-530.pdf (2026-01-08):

PDF generated with elabftw, (https://www.elabftw.net) a free and open source lab notebook File generated on 08-01-2026 at 09:15

## AE-530: Gas phase calibration of Normal range H2 sensor

Date: 2025-08-13
Tags: | Test | python | AE | Calibration | H2 | in-
situ | Unisense | electrochemical H2
detection
Category: H2 Evolution
Status: Done
Created by: Alexander Eith

## Literature/reference experiments

Literature | /
Reproduction | /
Similar experiments | H2 Evolution - AE-510: Gas phase test of H2 sensor (https://elab.water-splitting.org/experiments.php?mode=view&id=2400) H2 Evolution - AE-513: Gas and liquid phase calibration of H2 sensor (https://elab.water-splitting.org/experiments.php?mode=view&id=2513)

## Reagents

Name | CAS Number / Experiment Number | Inventory number | pressure [bar] | Volume | mass [g] | Concentration [M]
hydrogen | 1333-74-0 (https://commonchemistry.cas.org/detail?ref=1333-74-0) | / | approx. 1 | 2 ballon | / | /
Milli-Q water | / | / | / | 25 mL | / | /

## Procedure/observations

Date | Time | Step | Observations | Pictures
13.80 | | The gas phase calibration accoding to Protocol - Gas phase calibration of H2 UniAmp sensor (https://elab.water-splitting.org/database.php?mode=view&id=225) was started, with some deviations with Equipment - H2 UniAmp Sensor - Normal range - 2.1 x 80 mm needle. (https://elab.water-splitting.org/database.php?mode=view&id=256) The steps taken are shortly presented below with timestemps and deviations and observations. | / | /
| | The sensor was left connected to the device after H2 Evolution - AE-528: Initial test of H2 sensor (normal range), (https://elab.water-splitting.org/experiments.php?mode=view&id=2665) therefor no conditioning was needed and therefore not done here. Also the flask containing H2 was used from AE-528
| 13:40 | The setup with the H2/O2 reactor, the H2 sensor and the PT1000. The H2 sensor was connected using a 2 mm BOLA fitting. The reactor was filled with 25 mL water using a 20 mL syringe | The reactor was not totally dry after Prep work -AE-529: Volume determination of H2/O2 reactor (https://elab.water-splitting.org/experiments.php?mode=view&id=2675) | setup H2 sensor.jpg setup close up.jpg setup top view.jpg
| 14:17 | The H2 bubbling was resumed with a new ballon

14:20 | The logging was started with Pa as unit for the H2 content and a sample interval of 1 s | AE-530-1-logger1 | /
14:21 | The 0 ppm calibration point was taken | / | /
14:23 | H2 (0.06 mL) was added into the liquid using a 1 mL syringe | As volume of the gasphase 56.82 mL was assumed accroding to Prep work - AE-529: Volume determination of H2/O2 reactor (https://elab.water-splitting.org/experiments.php?mode=view&id=2675) | /
14:26 | The calibration point with 1056 ppm H2 was taken | Taken with intensity of 1.7 mV, noise level 0.25 mV | /
14:27 | H2 (0.56 mL) was added into the liquid using a 1 mL syringe | / | /
14:27 | The H2 bubbling was paused | / | /
14:29 | The calibration point with 10912 ppm H2 was taken | Taken with intensity of 10.7 mV | /
14:30 | H2 (1.0 mL) was added into the liquid using a 1 mL syringe | / | /
14:34 | A 2nd ballon was added to the H2 flask | / | with 2nd ballon.jpg
14:35 | The calibration point with 28511 ppm H2 was taken | Taken with intensity of 27.5 mV
14:36 | H2 (2 mL) was added into the liquid using a 2 mL syringe
14:39 | The calibration point with 63710 ppm H2 was taken | Taken with intensity of 58.0 mV
14:39 | H2 (3 mL) was added into the liquid using a 2 mL syringe
14:43 | The calibration point with 116508 ppm H2 was taken | Taken with intensity of 99.5 mV
14:44 | H2 (10 mL) was added into the liquid using a 20 mL syringe
14:47 | The calibration point with 292503 ppm H2 was taken | Taken with intensity of 209.7 mV

14:48 | A hydrogen ballon was atteched to the reactor and H2 bubbling was started | | cannula posiiton for H2 bubbling.jpg setup H2 bubbling in reactor.jpg
14:51 | The calibration point with 1.000.000 ppm H2 was taken | Taken with intensity of 1078 mV Noise similar to low range
14:52 | The H2 bubbling of the reactor was stopped
14:53 | The reactor was opened to the enviroment by opening the not used GL14 ports
| The calbiration was saved | AE-530-calib1 | /
| The calibration was saved without the 292503 ppm point | AE-530-calib2
15:16 | The logging was stopped | / | /

## Analysis

Date | Time | Sample name | Analysis method | Analytical device | Solvent | Raw Data | Processed Data | Comparative Data | Interpretation
13.08 | 14:20 | AE-530-1-logger1 | electrochemical H2 detection | Unisense H2 trace detector | water | AE-530-1.ulo g (http://elab.water-splitting.org/app/controllers/app/download.php?name=AE-530-1.ulog&storage=1) | AE-530-1-logger1.png AE-530-calib1.bmp AE-530-calib2.bmp | / | Worked well In total 8 point calibration was performed. 292503 ppm: to low signal: 2 possibiliteis: 1. error in amount H2 added (likely, due to use of 20 mL syringe), 2. error due to increased pressure, which was not shown in pressure sensor in device When taken all data points into account: slope: 0.011, intercept: -16.536, R2: 0.990 When ignoring datapoint at 292503 ppm: slope: 0.011, intercept: -6.389, R2: 1.000 Noise level cosistent at around 0.2 to 0.3 mV

## Results

Worked very well, linear up to 100 %

Good response, approx. detection limit 500 ppm, 50 Pa

## Linked experiments

H2 Evolution - AE-492: Liquid phase calibration of H2 sensor (https://elab.water-splitting.org/experiments.php?mode=view&id=2148)

H2 Evolution - AE-498: Liquid phase calibration of H2 sensor (https://elab.water-splitting.org/experiments.php?mode=view&id=2190)

H2 Evolution - AE-507: Liquid phase calibration of H2 sensor (https://elab.water-splitting.org/experiments.php?mode=view&id=2365)

H2 Evolution - AE-508: Gas phase calibration of H2 sensor (https://elab.water-splitting.org/experiments.php?mode=view&id=2385)

H2 Evolution - AE-510: Gas phase test of H2 sensor (https://elab.water-splitting.org/experiments.php?mode=view&id=2400)

H2 Evolution - AE-513: Gas and liquid phase calibration of H2 sensor (https://elab.water-splitting.org/experiments.php?mode=view&id=2513)

H2 Evolution - AE-522: Gas phase calibration of H2 sensor I (https://elab.water-splitting.org/experiments.php?mode=view&id=2609)

H2 Evolution - AE-528: Initial test of H2 sensor (normal range) (https://elab.water-splitting.org/experiments.php?mode=view&id=2665)

Prep work - AE-477: Testing of in-situ electrochemical hydrogen sensor and test H2 evolution reaction with RhCrO:Al:SrTiO3 (https://elab.water-splitting.org/experiments.php?mode=view&id=2029)

Prep work - AE-480: Testing of in-situ electrochemical H2 sensor from Unisense - gas phase and PT 100 (https://elab.water-splitting.org/experiments.php?mode=view&id=2069)

Prep work - AE-529: Volume determination of H2/O2 reactor (https://elab.water-splitting.org/experiments.php?mode=view&id=2675)

## Linked resources

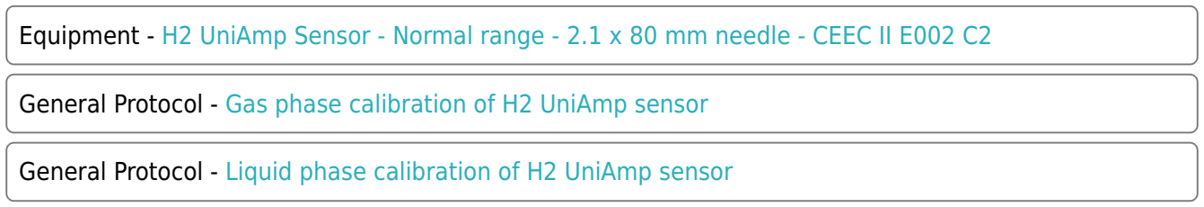
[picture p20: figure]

Equipment - H2 UniAmp Sensor - Normal range - 2.1 x 80 mm needle - CEEC II E002 C2 (https://elab.water-splitting.org/database.php?mode=view&id=256)

General Protocol - Gas phase calibration of H2 UniAmp sensor (https://elab.water-splitting.org/database.php?mode=view&id=225)

General Protocol - Liquid phase calibration of H2 UniAmp sensor (https://elab.water-splitting.org/database.php?mode=view&id=224)

## Attached files

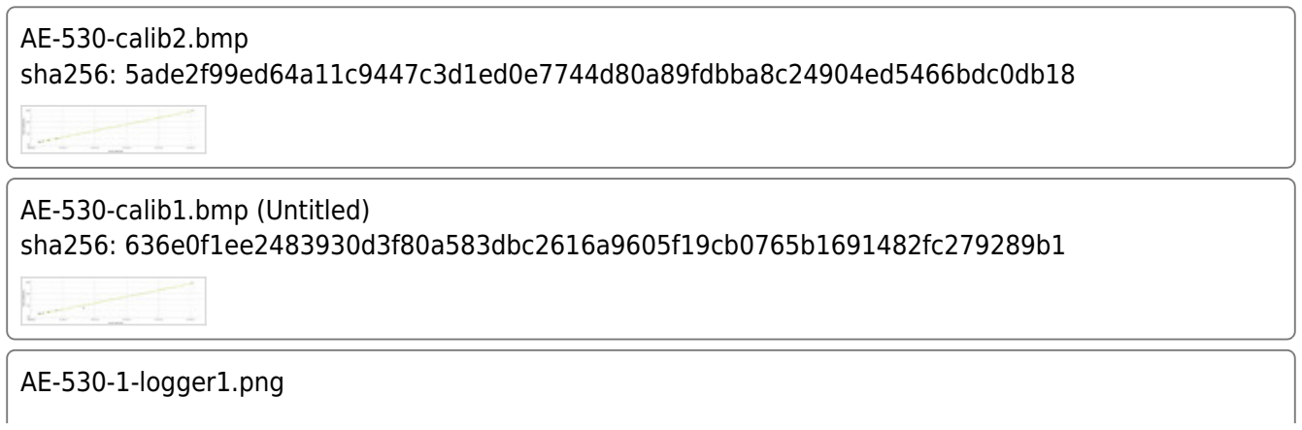
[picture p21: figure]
AE-530-calib2.bmp sha256: 5ade2f99ed64a11c9447c3d1ed0e7744d80a89fdbba8c24904ed5466bdc0db18; AE-530-calib1.bmp (Untitled) sha256: 636e0f1ee2483930d3f80a583dbc2616a9605f19cb0765b1691482fc279289b1; AE-530-1-logger1.png
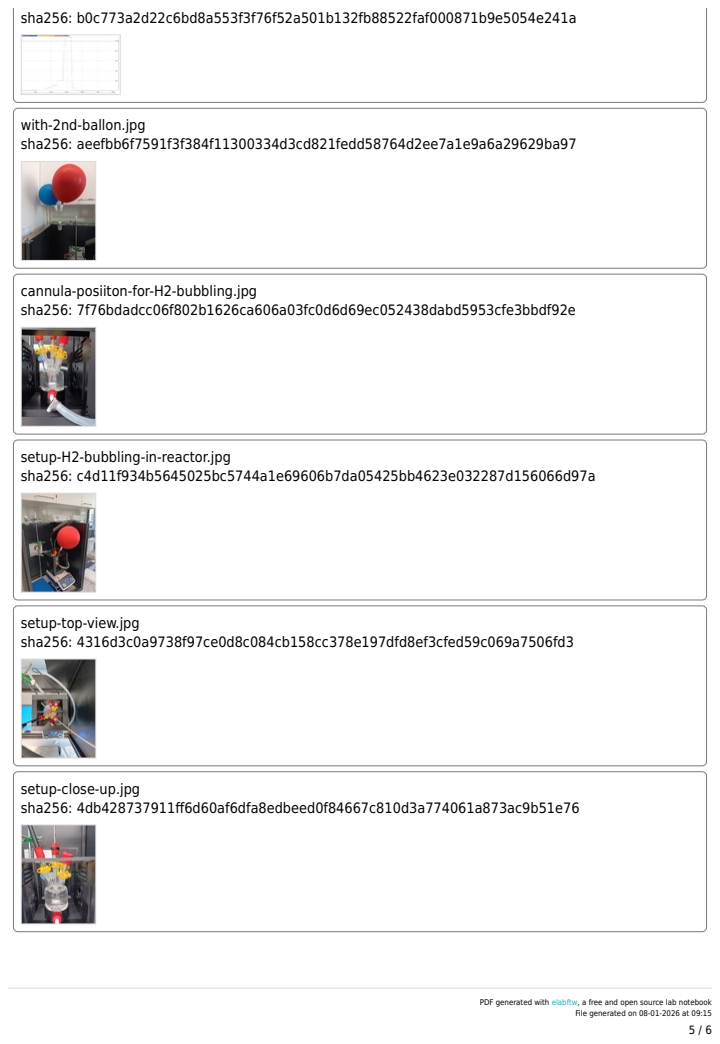
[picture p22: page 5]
sha256: b0c773a2d22c6bd8a553f3f76f52a501b132fb88522faf000871b9e5054e241a

with-2nd-ballon.jpg
sha256: aeefbb6f7591f3f384f11300334d3cd821fedd58764d2ee7a1e9a6a29629ba97

cannula-posiiton-for-H2-bubbling.jpg
sha256: 7f76bdadcc06f802b1626ca606a03fc0d6d69ec052438dabd5953cfe3bbdf92e

setup-H2-bubbling-in-reactor.jpg
sha256: c4d11f934b5645025bc5744a1e69606b7da05425bb4623e032287d156066d97a

setup-top-view.jpg
sha256: 4316d3c0a9738f97ce0d8c084cb158cc378e197dfd8ef3cfed59c069a7506fd3

setup-close-up.jpg
sha256: 4db428737911ff6d60af6dfa8edbeed0f84667c810d3a774061a873ac9b51e76

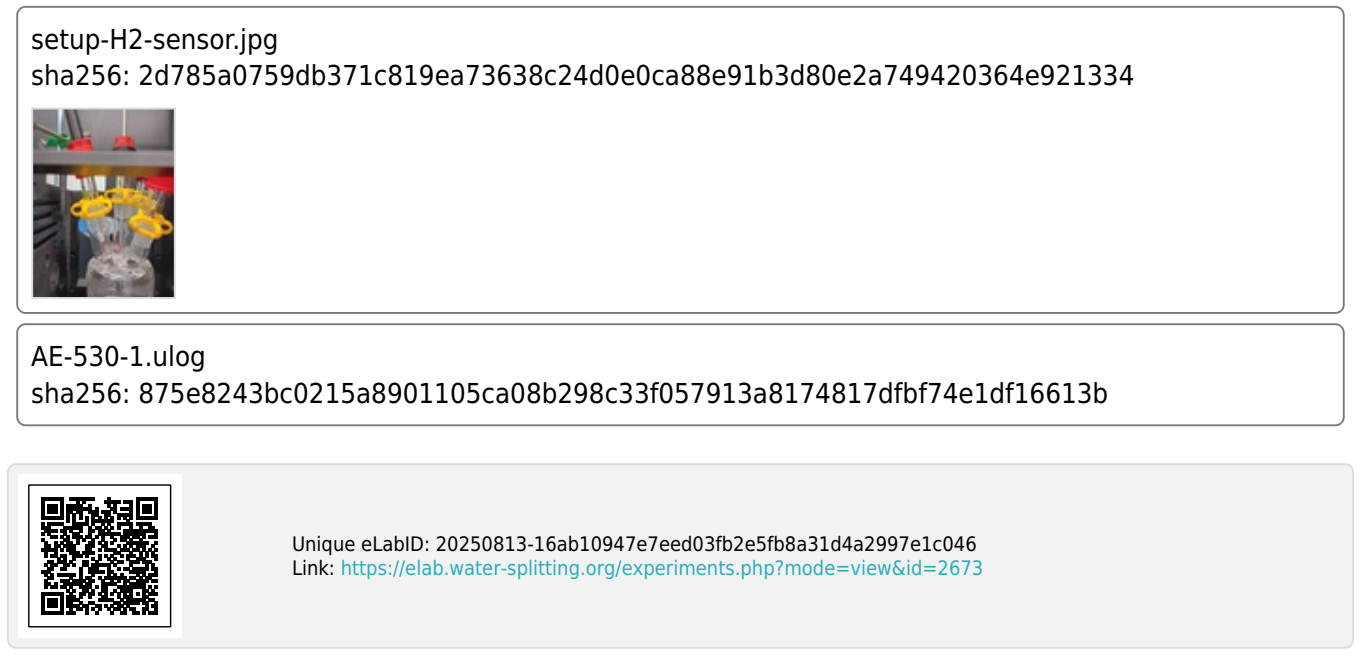
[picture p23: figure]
setup-H2-sensor.jpg sha256: 2d785a0759db371c819ea73638c24d0e0ca88e91b3d80e2a749420364e921334; AE-530-1.ulog sha256: 875e8243bc0215a8901105ca08b298c33f057913a8174817dfbf74e1df16613b; Unique eLabID: 20250813-16ab10947e7eed03fb2e5fb8a31d4a2997e1c046 Link: https://elab.water-splitting.org/experiments.php?mode=view&id=2673

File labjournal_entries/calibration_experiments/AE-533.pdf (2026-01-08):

PDF generated with elabftw, (https://www.elabftw.net) a free and open source lab notebook File generated on 08-01-2026 at 09:13

## AE-533: Liquid phase calibration in Argon of normal range H2 sensor

Date: 2025-08-18
Tags: | Test | AE | Calibration | H2 | in-situ
Unisense | electrochemical H2 detection
H2/O2 reactor
Category: Prep work
Status: Done
Created by: Alexander Eith

## Literature/reference experiments

Literature | /
Reproduction | /
Similar experiments | H2 Evolution - AE-531: Liquid phase calibration of normal range H2 sensor (https://elab.water-splitting.org/experiments.php?mode=view&id=2674)

## Reagents

Name | CAS Number / Experiment Number | Inventory number | pressure [bar] | Volume [ml] | mass [g] | Concentration [M]
hydrogen | 1333-74-0 (https://commonchemistry.cas.org/detail?ref=1333-74-0) | / | approx. 1 | 2 ballons | / | /
Milli-Q water | / | / | / | 25 | / | /

## Procedure/observations

Date | Time | Step | Observations | Pictures
18.08 | | The liquid phase calibration accoding to Protocol - Liquid phase calibration of H2 UniAmp sensor (https://elab.water-splitting.org/database.php?mode=view&id=224) was started, with some deviations with Equipment - H2 UniAmp Sensor - Normal range - 2.1 x 80 mm needle. (https://elab.water-splitting.org/database.php?mode=view&id=256) The steps taken are shortly presented below with timestemps and deviations and observations. | / | /

09:05

The setup was build using the H2/O2 reactor, the PT1000 connected to the Equipment - H2 UniAmp Single Channel System, (https://elab.water-splitting.org/database.php?mode=view&id=221) and a Equipment - Firesting Fiber-Optic Oxygen Meter 2 Channel (Firesting 2) (https://elab.water-splitting.org/database.php?mode=view&id=166) with the Equipment - Robust probe for liquid O2 measurment (https://elab.water-splitting.org/database.php?mode=view&id=173) and a PT100. The PT100 was placed outsidethe reactor in the advanced irradiatio setup. PTFE tubing was connected to the valve, which was connected to an argon line. The H2 sensor was placed outside of the reactor. The stll open GL connections wereclosed with GL caps
The reactor was filled with water (25 mL) using a 25 mL graduated cylinger
for picture see 09:34 | /
09:23 | The oxygen log on the firesting was started | AE-533-1-O2 | /
09:34 | The degassing of the H2/O2 reactor with argon was started | / | setup ar sparging.jpg

09:35 | The hydrogen log was started | AE-533-1-H2-logger1 | /
09:41 | In a 5 mL rbf water (approx. 5 mL) was added and a hydrogen ballon was connected, starting the hydrogen bubbling | / | setup H2 bubbling.jpg top left rbf for H2 bubbling.jpg
09:52 | The hydrogen log was stopped | / | /
09:53 | The H2 sensor was moved to the H2/O2 reactor in Argon counterflow | / | setup for calibration.jpg setup for calibration side view.jpg
09:54 | The hydrogen log was started | AE-533-1-H2-logger2 | /
09:55 | The degassing of the H2/O2 reactor was stopped | / | /
09:59 | The 0 ppm H2 saturated water point was taken | 0.7 mV | /
10:00 | Hydrogen saturated water was added (0.25 mL) to the reactor using 1 mL syringe | / | /
10:01 | The 9901 ppm H2 saturated water point was taken | 10 mV | /
10:01 | Hydrogen saturated water was added (1.0 mL) to the reactor using 1 mL syringe | / | /
10:02 | The 47619 ppm calibration point was taken | 38.5 mV | /
10:03 | A hydrogen ballon was atteched to the reactor and H2 bubbling was started. After approx 5 min the ballon was exchanged by a new Hydrogen ballon | / | setup H2 bubbling in reactor close up.jpg setup H2 bubbling in reactor.jpg
10:17 | The calibration point with 1.000.000 ppm H2 was taken | 1108 mV | /
10:18 | The H2 bubbling of the reactor was stopped | / | /
10:19 | The reactor was opened to the enviroment | / | /
| The calibration was saved with all data points | AE-533-calib-all_data.bmp | /
| The calibration was saved without 1.000.000 ppm points | AE-533-calib_without_1000000ppm.bmp | /
| The calibration was saved without 47619 ppm points | AE-533-calbi_without 47619ppm.bmp | /
| The calibration was saved without 47619 and 1.000.000 ppm points | AE-533-calib_wothout_1000000_and_47619ppm.bmp | /
10:20 | The H2/O2 reactor as flushed with argon | / | /
10:?0 | The logging of O2 and H2 was stopped | / | /

## Analysis

Date | Time | Sample name | Analysis method | Analytical device | Solvent | Raw Data | Processed Data | Comparative Data | Interpretation
18.08 | 09:23 | AE-533-1-H2-logger1 | electrochemical H2 detection | Equipment - H2 UniAmp Sensor -Normal range - 2.1 x 80 mm needle (https://elab.water-splitting.org/database.php?mode=view&id=256) | water | AE-533-1-H2.ulog (http://elab.water-splitting.org/app/controllers/app/download.php?name=AE-533-1-H2.ulog&storage=1) | AE-533-1-H2-logger1.png | H2 Evolution -AE-531: Liquid phase calibration of normal range H2 sensor (https://elab.water-splitting.org/experiments.php?mode=view&id=2674) | Stable after approx. 10 min, signal of 0.7 mV
18.08 | 09:25 | AE-533-1-H2-logger1 | electrochemical H2 detection | Equipment - H2 UniAmp Sensor -Normal range - 2.1 x 80 mm needle (https://elab.water-splitting.org/database.php?mode=view&id=256) | water | AE-533-1-H2.ulog (http://elab.water-splitting.org/app/controllers/app/download.php?name=AE-533-1-H2.ulog&storage=1) | AE-533-1-H2-logger-2.png AE-533-calib-all_data.bmp AE-533-calib_without_1000000ppm.bmp AE-533-calbi_without 47619ppm.bmp AE-533-calib_wothout_1000000_and_47619ppm.bmp | H2 Evolution -AE-531: Liquid phase calibration of normal range H2 sensor (https://elab.water-splitting.org/experiments.php?mode=view&id=2674) | all data: slope: 1.436, Intercept: -4.822, R2: 1.000 w/o 1.000.000 ppm: slope 1.001, intercept: 1.456, R2: 0.999 w/o 47619 ppm: slope: 1.433, intercept: -0.111, R2: 1.000 w/o 1.000.000 and 47619 ppm: slope: 1.174, intercept: 0.873, R2: 1.000
18.08 | 09:54 | AE-533-1-O2 | Optical O2 detection | Equipment - Firesting Fiber-Opitc Oxygen Meter 2 Channel (https://elab.water-splitting.org/database.php?mode=view&id=90) | water | AE-533-1-O2.txt (http://elab.water-splitting.org/app/controllers/app/download.php?name=2025-08-18_092351_AE-533-1-O2.txt&storage=1) | AE-533-1-O2.png | / | Degassing worked till 0.6 µM, increase to 2 µM upon stopping, decrease to approx. 1 µM upon H2 bubbling

## Results

Worked nicely, similar slope obtained compared to AE-531. Good linearity obtained.

O2 measuremnt during H2 bubbling shows only minor amounts of H2 in ballon and also in H2 saturated water low amount of O2, since no spike upon addition of H2 saturated water was observed

### Linked experiments

H2 Evolution - AE-492: Liquid phase calibration of H2 sensor (https://elab.water-splitting.org/experiments.php?mode=view&id=2148)

H2 Evolution - AE-498: Liquid phase calibration of H2 sensor (https://elab.water-splitting.org/experiments.php?mode=view&id=2190)

H2 Evolution - AE-504: Liquid phase calibration of H2 sensor I (https://elab.water-splitting.org/experiments.php?mode=view&id=2221)

H2 Evolution - AE-528: Initial test of H2 sensor (normal range) (https://elab.water-splitting.org/experiments.php?mode=view&id=2665)

H2 Evolution - AE-530: Gas phase calibration of Normal range H2 sensor (https://elab.water-splitting.org/experiments.php?mode=view&id=2673)

H2 Evolution - AE-531: Liquid phase calibration of normal range H2 sensor (https://elab.water-splitting.org/experiments.php?mode=view&id=2674)

Prep work - AE-477: Testing of in-situ electrochemical hydrogen sensor and test H2 evolution reaction with RhCrO:Al:SrTiO3 (https://elab.water-splitting.org/experiments.php?mode=view&id=2029)

### Linked resources

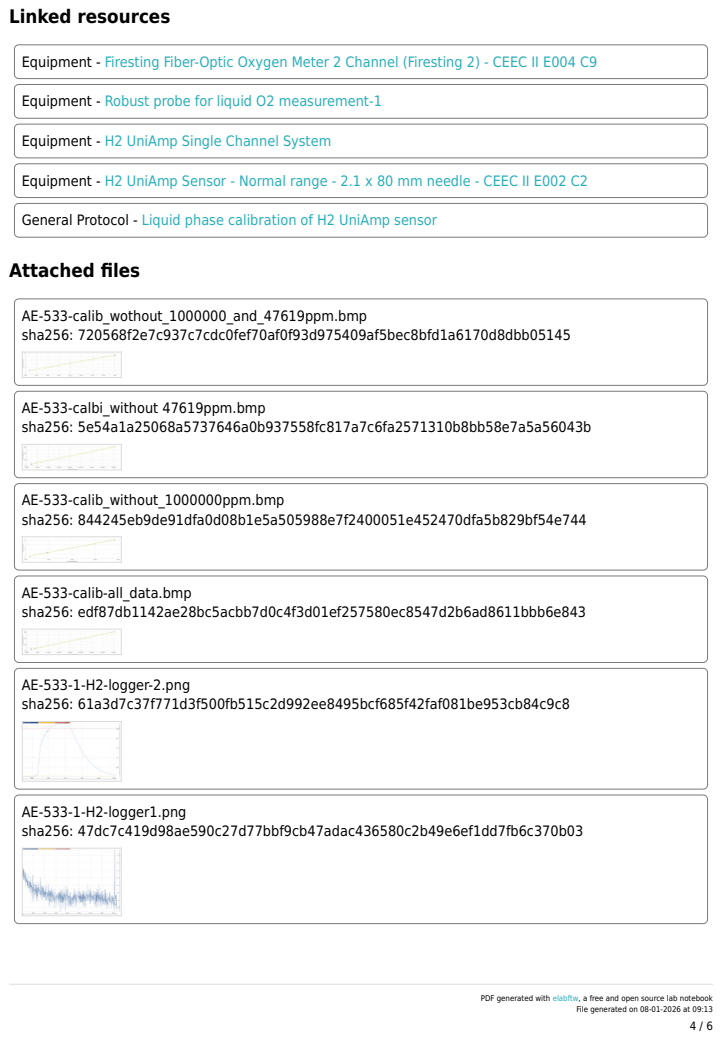
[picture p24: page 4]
Attached files; AE-533-calib_wothout_1000000_and_47619ppm.bmp sha256: 720568f2e7c937c7cdc0fef70af0f93d975409af5bec8bfd1a6170d8dbb05145; AE-533-calbi_without 47619ppm.bmp sha256: 5e54a1a25068a5737646a0b937558fc817a7c6fa2571310b8bb58e7a5a56043b; AE-533-calib_without_1000000ppm.bmp sha256: 844245eb9de91dfa0d08b1e5a505988e7f2400051e452470dfa5b829bf54e744; AE-533-1-H2-logger1.png sha256: 47dc7c419d98ae590c27d77bbf9cb47adac436580c2b49e6ef1dd7fb6c370b03

Equipment - Firesting Fiber-Optic Oxygen Meter 2 Channel (Firesting 2) - CEEC II E004 C9 (https://elab.water-splitting.org/database.php?mode=view&id=166)

Equipment - Robust probe for liquid O2 measurement-1 (https://elab.water-splitting.org/database.php?mode=view&id=173)

Equipment - H2 UniAmp Single Channel System (https://elab.water-splitting.org/database.php?mode=view&id=221)

Equipment - H2 UniAmp Sensor - Normal range - 2.1 x 80 mm needle - CEEC II E002 C2 (https://elab.water-splitting.org/database.php?mode=view&id=256)

General Protocol - Liquid phase calibration of H2 UniAmp sensor (https://elab.water-splitting.org/database.php?mode=view&id=224)

AE-533-calib-all_data.bmp
sha256: edf87db1142ae28bc5acbb7d0c4f3d01ef257580ec8547d2b6ad8611bbb6e843

AE-533-1-H2-logger-2.png
sha256: 61a3d7c37f771d3f500fb515c2d992ee8495bcf685f42faf081be953cb84c9c8

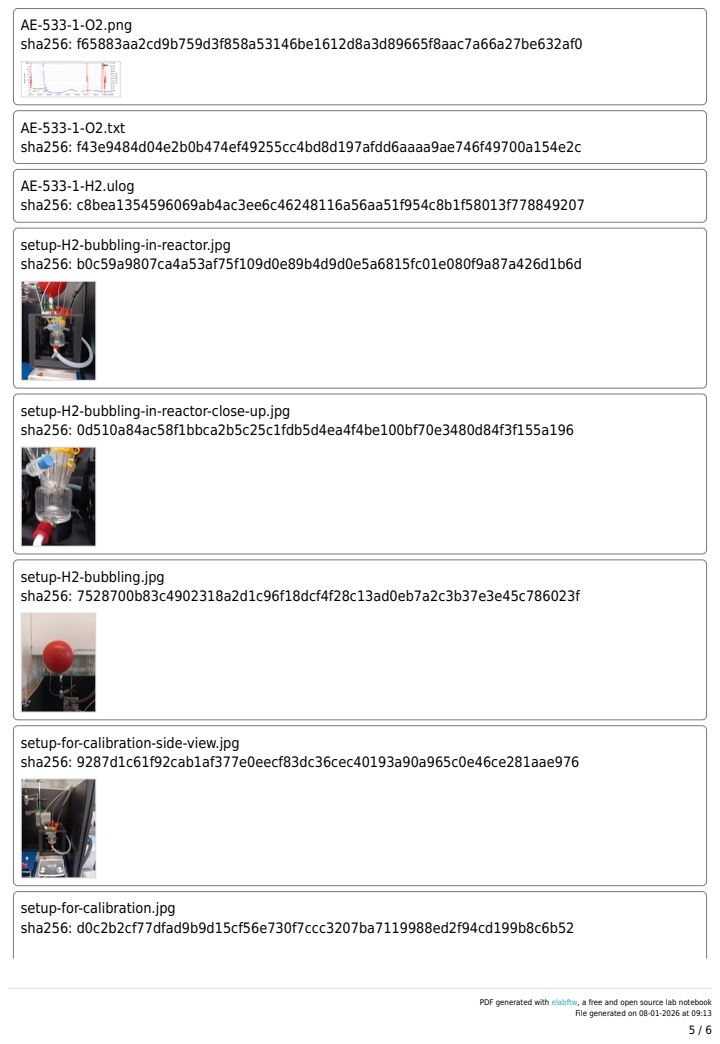
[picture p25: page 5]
AE-533-1-O2.png sha256: f65883aa2cd9b759d3f858a53146be1612d8a3d89665f8aac7a66a27be632af0; AE-533-1-O2.txt sha256: f43e9484d04e2b0b474ef49255cc4bd8d197afdd6aaaa9ae746f49700a154e2c; AE-533-1-H2.ulog sha256: c8bea1354596069ab4ac3ee6c46248116a56aa51f954c8b1f58013f778849207

setup-H2-bubbling-in-reactor.jpg
sha256: b0c59a9807ca4a53af75f109d0e89b4d9d0e5a6815fc01e080f9a87a426d1b6d

setup-H2-bubbling-in-reactor-close-up.jpg
sha256: 0d510a84ac58f1bbca2b5c25c1fdb5d4ea4f4be100bf70e3480d84f3f155a196

setup-H2-bubbling.jpg
sha256: 7528700b83c4902318a2d1c96f18dcf4f28c13ad0eb7a2c3b37e3e45c786023f

setup-for-calibration-side-view.jpg
sha256: 9287d1c61f92cab1af377e0eecf83dc36cec40193a90a965c0e46ce281aae976

setup-for-calibration.jpg
sha256: d0c2b2cf77dfad9b9d15cf56e730f7ccc3207ba7119988ed2f94cd199b8c6b52

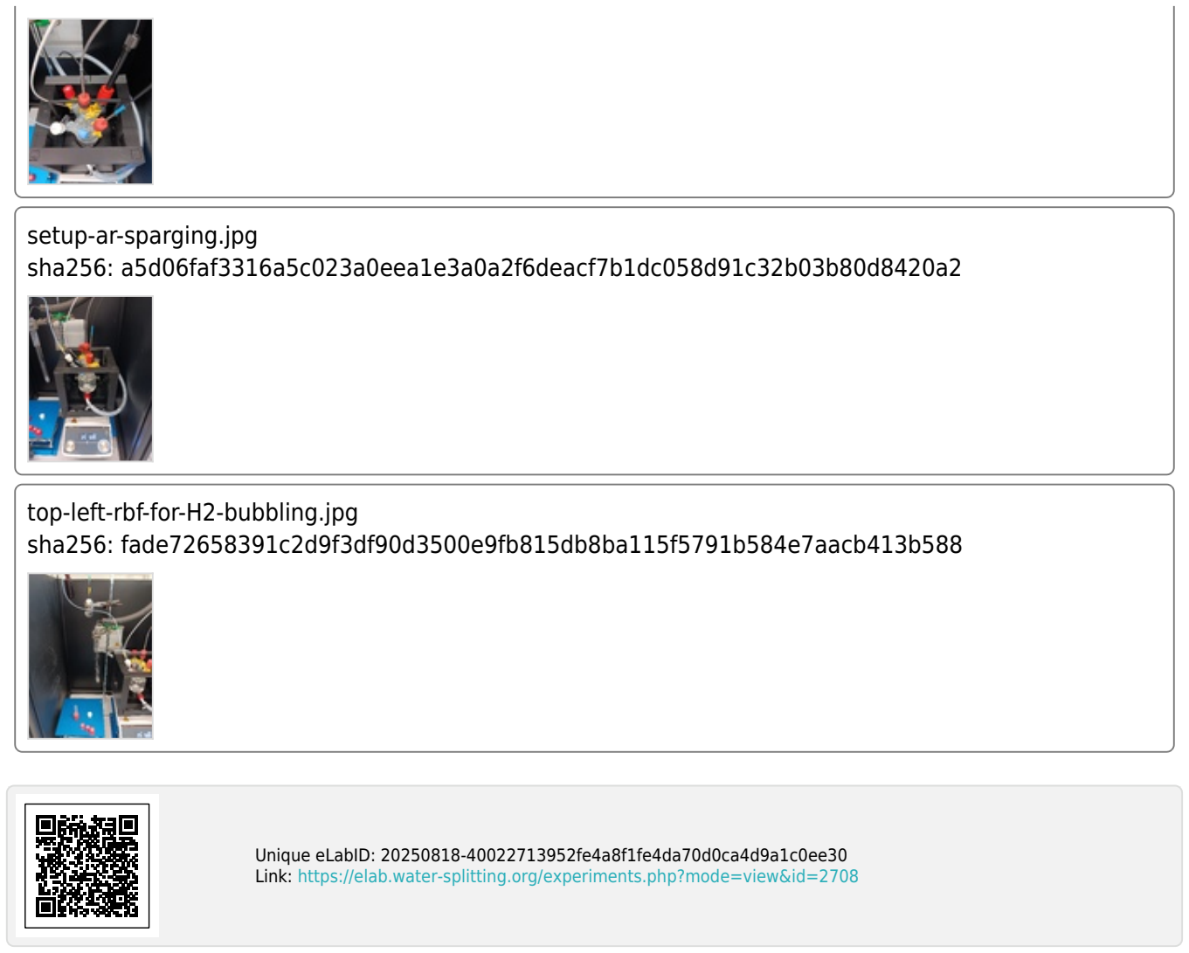
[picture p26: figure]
setup-ar-sparging.jpg sha256: a5d06faf3316a5c023a0eea1e3a0a2f6deacf7b1dc058d91c32b03b80d8420a2; top-left-rbf-for-H2-bubbling.jpg sha256: fade72658391c2d9f3df90d3500e9fb815db8ba115f5791b584e7aacb413b588; Unique eLabID: 20250818-40022713952fe4a8f1fe4da70d0ca4d9a1c0ee30 Link: https://elab.water-splitting.org/experiments.php?mode=view&id=2708

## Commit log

2025-11-19 Start of Git repository for the O2/H2 reactor. Addition of labjournal entries for gerneral protocols and equipment, as well as for the irradiation chamber
2025-11-20 addition of documentaiton for the irradiation setup
    [aperture_double_walled_beaker_v1-0.ipt, aperture_double_walled_beaker_v1-0.stl, aperture_dummy_v1-0.ipt, aperture_dummy_v1-0.stl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]
2025-11-28 adding of READMEs to subsubfolders in irradiation_setup, correction of spelling errors in irradiation_setup, changeing pptx files in figures against png files
    [aperture_dummy_v1-0.ipt, aperture_dummy_v1-0.stl, aperture_led_v1-0.ipt, aperture_led_v1-0.stl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]
2025-11-30 Uploading O2 and H2 data files (txt and csv)
    [NB-312-Logger3-Data (1 H2 UniAmp (503157)).csv, NB-316-Logger2-during irradiation.csv, NB-318-Logger1.csv, NB-319-Logger3-during irradiation.csv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]
2025-11-30 Upload O2_H2_overview file
    [251126_O2_H2_Experiment_Overview.xlsx]
2025-12-04 Update irradiation_data folder
    [251126_O2_H2_Experiment_Overview.xlsx, 251204_O2_H2_Experiment_Overview.xlsx, NB-365-Logger3-during irradiation.csv, NB-366-Logger1.csv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]
2026-01-07 Adding BET data
    [BET _N2_77_K-ads.csv, BET _N2_77_K-des.csv]
2026-01-07 Adding calibration data
2026-01-08 Adding labjournal entries-calibration data
2026-01-08 Updating calibration data
